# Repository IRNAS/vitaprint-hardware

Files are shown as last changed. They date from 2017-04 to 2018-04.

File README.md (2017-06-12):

# Vitaprint extruder

This repository containst files and descriptions for building a stepper-motor powered syringe extruder, which can be mounted on a general use CNC system. Feel free to fork and comment and if you have any questions, you [contact us](mailto:banovic@irnas.eu) directly. Contained in the repository you will find design files, a bill of materials, assembly instructions and extrusion calibration. To use the extruder within a CNC system, you will require CNC control electronics and software, which we do not provide. At Symbiolab the extruder was tested with [PlanetCNC](https://planet-cnc.com/).

## License 

All our projects are as usefully open-source as possible.

Hardware including documentation is licensed under [CERN OHL v.1.2. license](http://www.ohwr.org/licenses/cern-ohl/v1.2)

Firmware and software originating from the project is licensed under [GNU GENERAL PUBLIC LICENSE v3](http://www.gnu.org/licenses/gpl-3.0.en.html).

Open data generated by our projects is licensed under [CC0](https://creativecommons.org/publicdomain/zero/1.0/legalcode).

All our websites and additional documentation are licensed under [Creative Commons Attribution-ShareAlike 4 .0 Unported License] (https://creativecommons.org/licenses/by-sa/4.0/legalcode).

What this means is that you can use hardware, firmware, software and documentation without paying a royalty and knowing that you'll be able to use your version forever. You are also free to make changes but if you share these changes then you have to do so on the same conditions that you enjoy.

Symbiolab, Koruza, GoodEnoughCNC and IRNAS are all names and marks of Institut IRNAS Rače.
You may use these names and terms only to attribute the appropriate entity as required by the Open Licences referred to above. You may not use them in any other way and in particular you may not use them to imply endorsement or authorization of any hardware that you design, make or sell.



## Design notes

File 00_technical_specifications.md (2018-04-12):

# Vitaprint hardware technical specifications

## CNC XYZ mechanics: 3020T
- Machine size:
  -- Width: 410mm (X)
  -- Depth: 540mm (Y)
  -- Height: 400mm (Z)
- Motors (x, y, z):  NEMA23
- Movement resolution: 0.01mm (theoretically achievable 0.001mm)
- Motion drive: trapeziodal lead screw, linear rods with ball bearings
- Maximal number of extruders: 3

NOTE: The values above are for a default setup. Extrudes can be mounted on any 3-axis CNC platform, therefore the working area and maximal number of extruders can be changed if needed.

## Vitaprint extruder:
- Axis: 2
- Motion: Extruder Z movement and E extrusion
- Z motor: NEMA 11
- E motor: NEMA 11 with planetary gearbox
- Z movement resolution: 0.01mm (theoretically achievable 0.001mm)
- Cartridge: 5ml luer-lock syringes (polypropylene)
- Nozzle: Gauge needle
- Heating: room temperature - 250°C
- Extrusion resolution: 0.01mm piston movement (1.2uL for 5ml syringe)

## Control electronics:
- Controller: PlanetCNC MK3 9 axis
- Control software: PlanetCNC CNC USB controller
- Power Requirements: 230/110V AC
- Software: PlanetCNC CNC USB controller
- Operating Systems: Windows / Linux
- Print File Type: G-code

## Printing:
- Printing volume (x,y,z): 200 x 300 x 45mm
- Printing speed: max 2600mm/min, typical 500mm/min
- Print File Type: G-code (generate externally via Slic3r software)

NOTE: printing volume will depend on the amount of extruders used.

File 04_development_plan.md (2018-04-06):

# Vitaprint development plan:

## Biofabrication tools
- Microextrusion:
  * Piston driven syringe extrusion - standard syringes of various sizes (5 - 20ml)
  * Hydraulic syringe extrusion
  * Screw valve extrusion
- Core-shell printing
  * Needle in needle
- Multi-component printing
- Laser techniques
- Electrospinning
- Multiphoton polymerization
  
## Printer upgrades
- Thermoregulation: 
  * bed
  * nozzle
  * atmospheric chamber
- Bed: 
 * vacuum adhesion
 * dish positioning and adhesion
 * Autoleveling
- Monitoring:
  * Video microscope
  * Flow rate
  * Cartridge pressure

## Software add-ons and upgrades 
- g-code post-processing development for slicing software (eg. Slic3r, Cura,...)
- manual flow regulation of g-code embedded extrusion
- algorithmic extrusion linearization
- calibration protocols
- material optimization algortihms and methods
- Adaptive printing

## Fabrication protocol database
- Hydrogels
  * Gelatin
  * Collagen
  * Alginate
  * Chitosan
  * Gluten
  * Gellan gum  
  * Xanthan gum
  * Silk fibroin
  
- Pastes
  * Hydroxiapatite
  
- Polymers
  * Polycaprolactone
  * Polylactic acid

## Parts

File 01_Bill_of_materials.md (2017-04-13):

# Bill of materials

## Housing:
 - Aluminium plates (300mm x 400mm x 5mm)
 - Aluminium blocks:
   - SYRINGE MOUNT: block 35mm x 45mm x 70mm (minimum)
   - FRONT CAP: block 40mm x 12mm x 60mm (minimum)
   - 24BYJ48 NUT: block 15mm x 25mm x 30mm (minimum)
 - M3x12 DIN965 philips screw 10 pcs
 - M3x12 BN6404 torx sxrew 20pcs
 - 2 x fi3 stainless steel rod (L = 110mm)
 - 40mm x 8mm x 2mm rubber sheet

## Movement
 - Stepper motor Nema11 planetary (1:5 gear ratio)
 - 28BYJ48 unipolar motor ([modified into a bipolar motor] http://www.jangeox.be/2013/10/change-unipolar-28byj-48-to-bipolar.html )
 - Linear rail with carrige (L = 100mm)
 - Sliding rods (stainles steel, fi 3mm)
 - Brass spindle (M5x0.5mm, L = 90mm)
 - NUT: 3D printed 100% infill ABS block (28x28x55mm)

## Thermoregulation
 - Thermistor (read how to calibrate your own thermistor in the Calibration section)
 - 40W ceramic heater for 3D printers
 - 24V DC power supply
 - In our iteration we used PID thermoregulation algorithm (parameters need to be tuned by the user, depending on the control setup). Other temperature control systems can also be applied with this given hardware (relay switchin etc.).

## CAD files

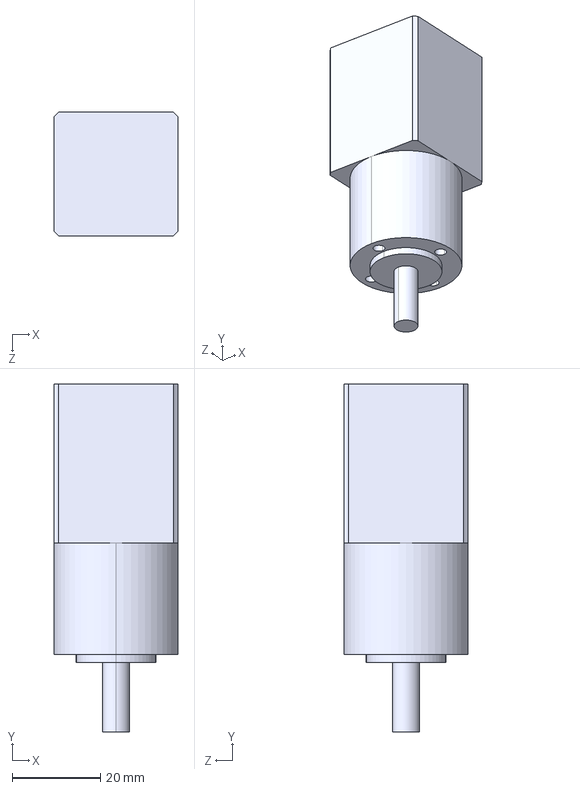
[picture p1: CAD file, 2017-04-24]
Build_files/Nema11_planetary.STEP
28.0 x 78.7 x 28.0 mm

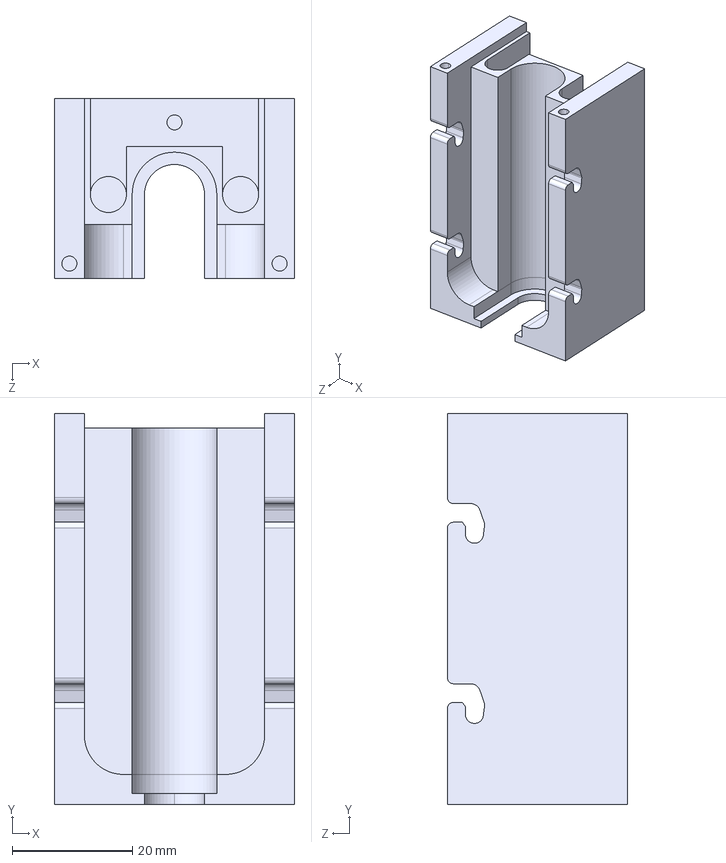
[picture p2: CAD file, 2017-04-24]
Build_files/syringe_mount.STEP
40.0 x 65.1 x 30.0 mm

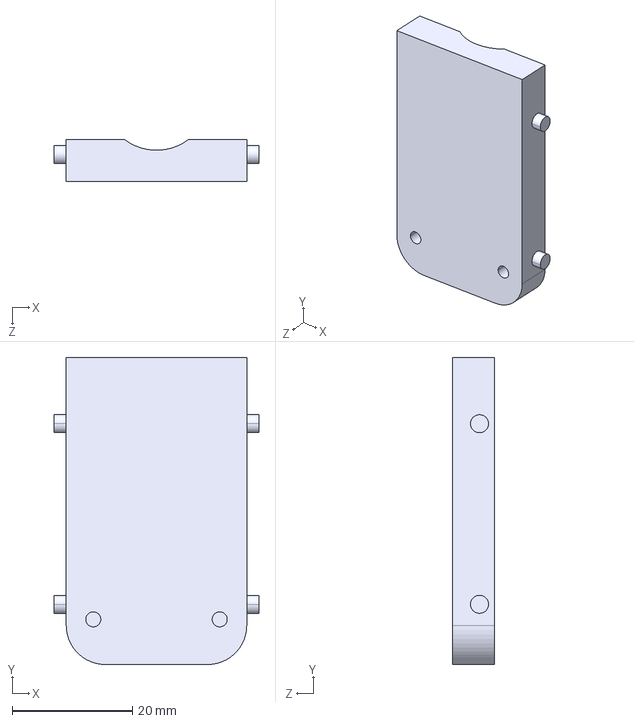
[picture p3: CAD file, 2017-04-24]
Build_files/front_cap.STEP
34.0 x 51.0 x 7.00 mm

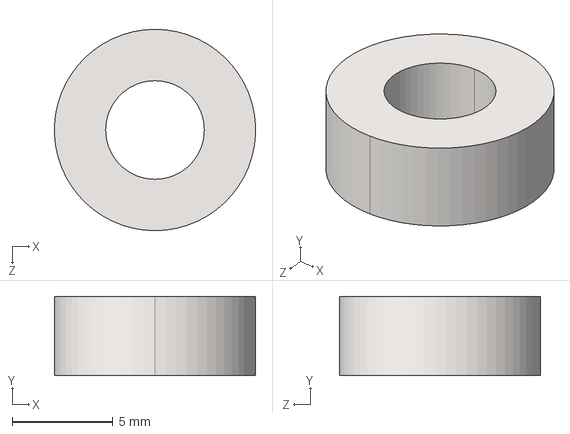
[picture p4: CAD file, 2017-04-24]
Build_files/rod_bearing.STEP
9.99 x 3.94 x 10.0 mm

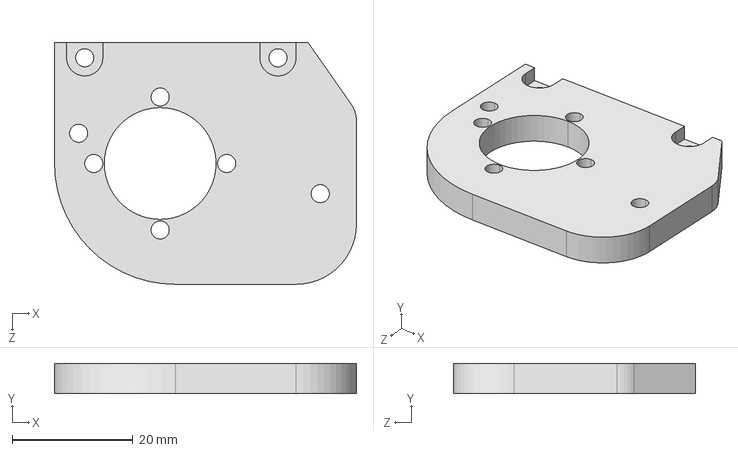
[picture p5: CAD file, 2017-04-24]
Build_files/N11-motor_plate_right.STEP
50.0 x 5.00 x 40.0 mm

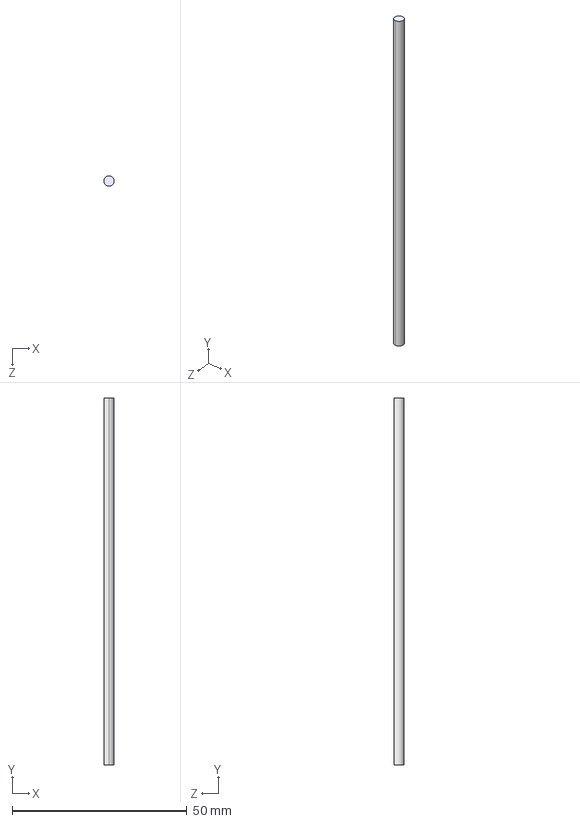
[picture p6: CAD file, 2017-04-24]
Build_files/rod fi3.STEP
3.00 x 105.0 x 3.00 mm

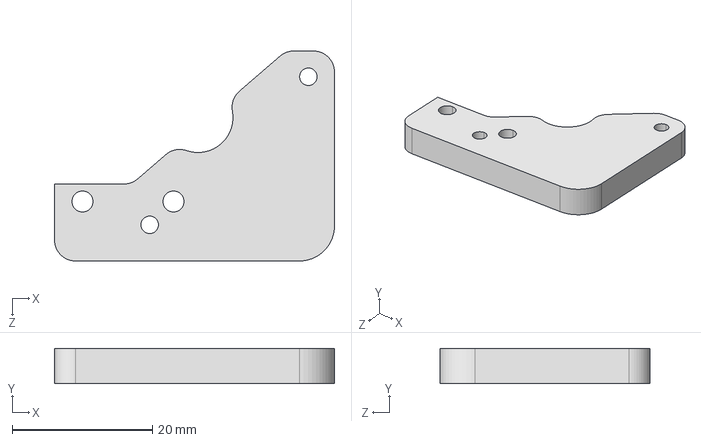
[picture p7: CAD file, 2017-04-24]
Build_files/24BYJ48-motor_plate_right.STEP
40.0 x 5.00 x 30.0 mm

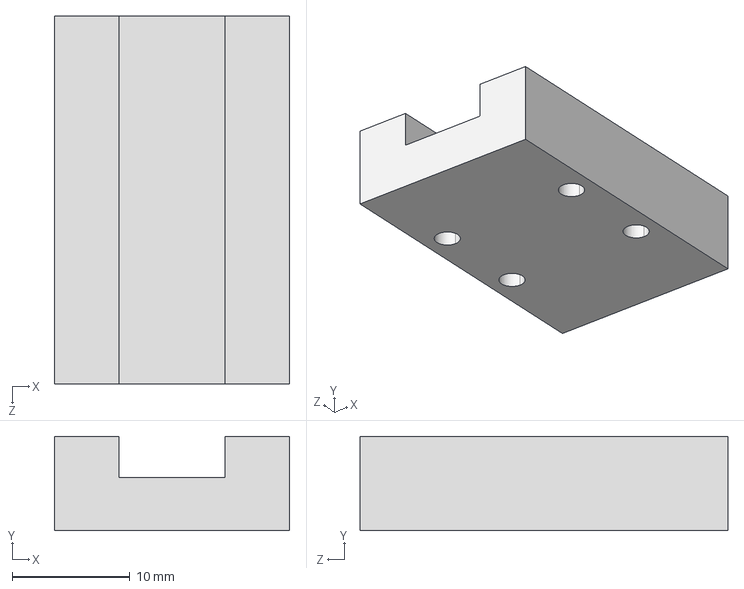
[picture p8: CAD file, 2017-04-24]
Build_files/trolley.STEP
20.0 x 8.00 x 31.3 mm

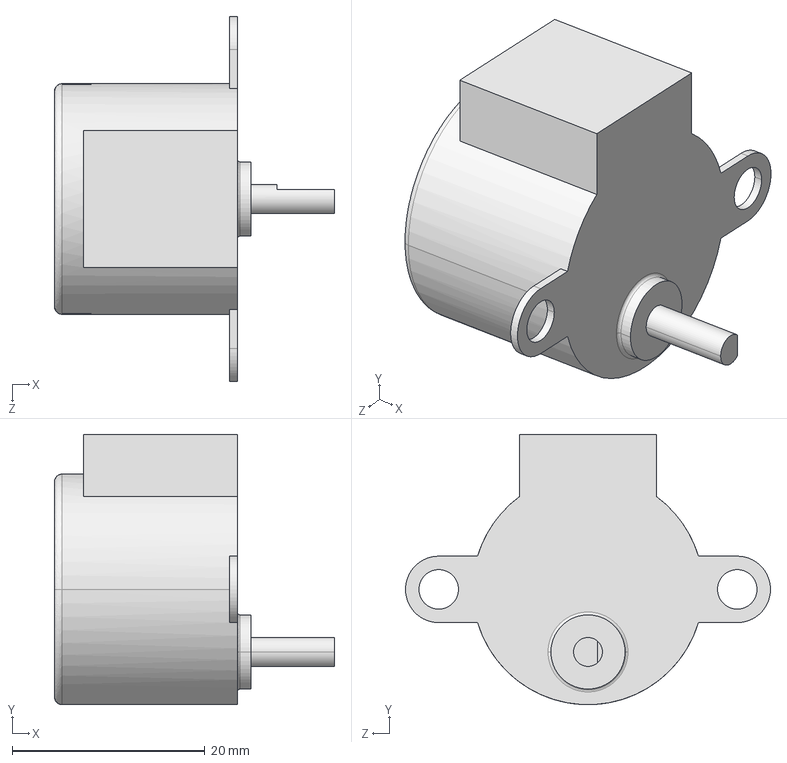
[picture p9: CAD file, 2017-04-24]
Build_files/24BYJ48-stepper.STEP
29.1 x 28.1 x 37.9 mm

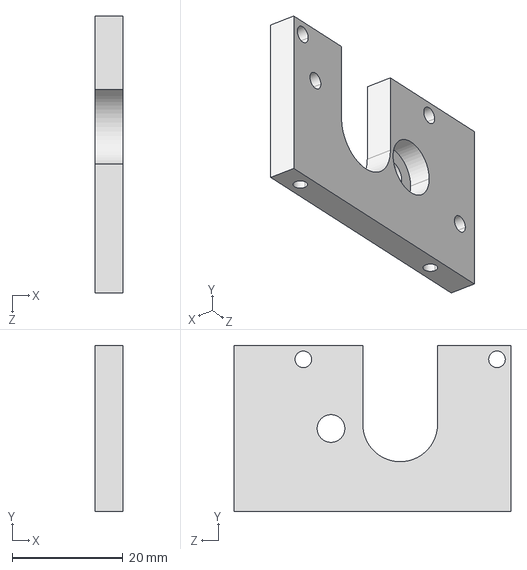
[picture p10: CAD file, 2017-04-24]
Build_files/rod_holder_right.STEP
5.00 x 30.0 x 50.0 mm

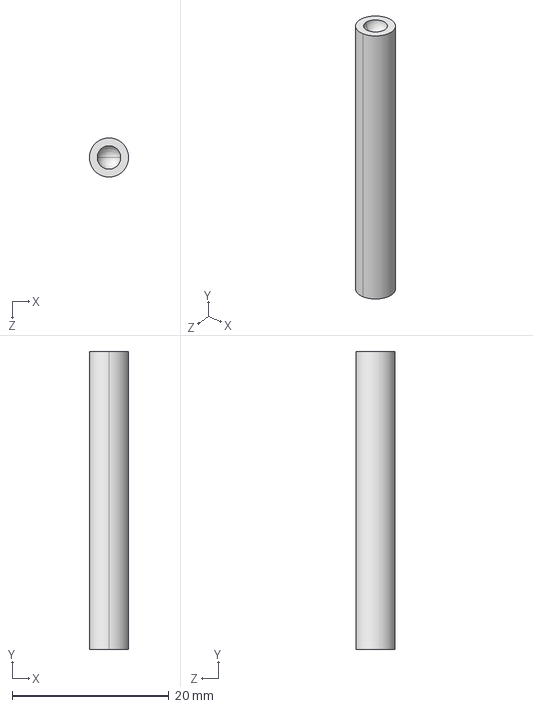
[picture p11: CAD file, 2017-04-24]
Build_files/24BYJ48_threaded_rod.STEP
5.00 x 38.0 x 5.00 mm

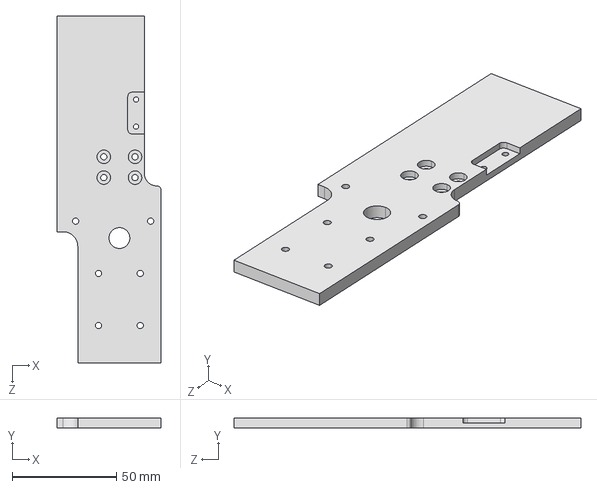
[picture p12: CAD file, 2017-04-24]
Build_files/backplate_right.STEP
50.0 x 5.00 x 166.6 mm

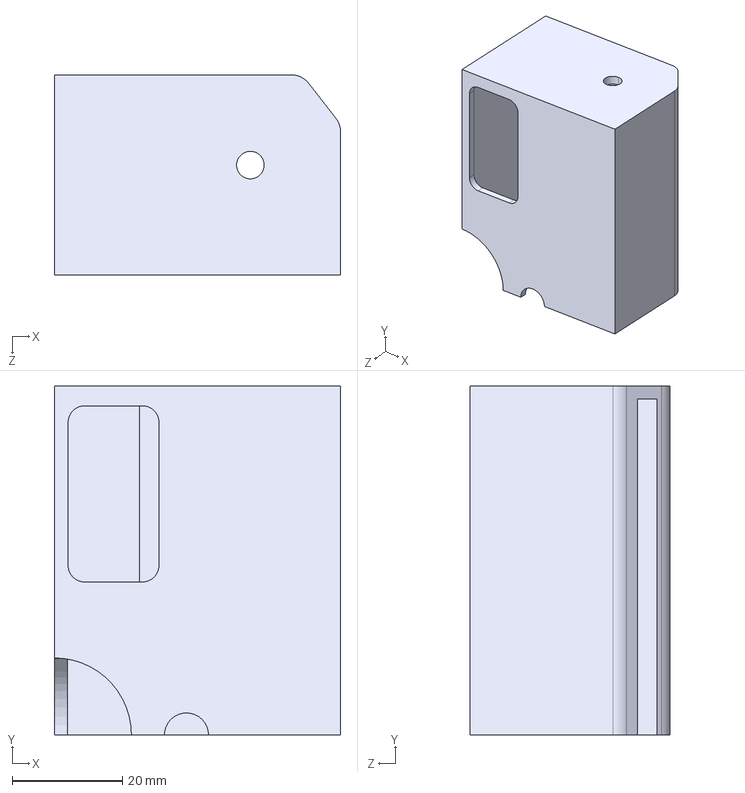
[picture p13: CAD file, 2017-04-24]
Build_files/cable_box-Mirror11.STEP
52.0 x 63.4 x 36.4 mm

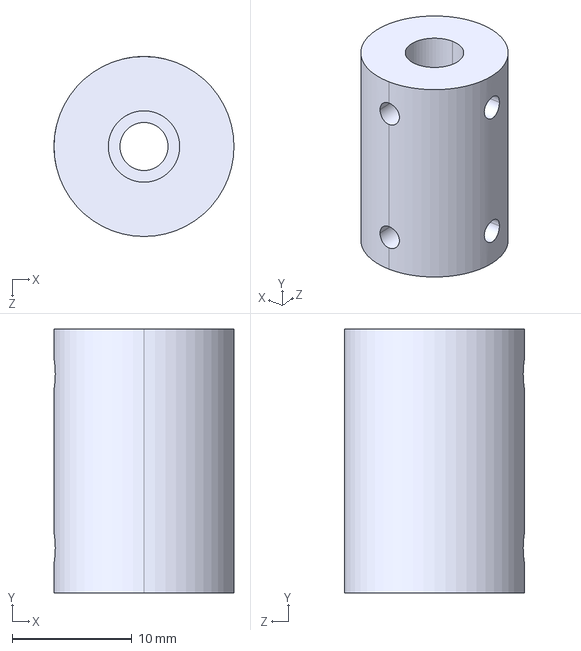
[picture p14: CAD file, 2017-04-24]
Build_files/coupler_extruder.STEP
15.0 x 22.0 x 15.0 mm

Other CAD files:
Build_files/N11-motor-plate_left.STEP
Build_files/24BYJ48-motor_plate_left.STEP
Build_files/backplate_left.STEP
Build_files/24BYJ48_nut.STEP
Build_files/Nut-block.STL
Build_files/cable_box-Boss-Extrude1.STEP
Build_files/nut - left.STEP
Build_files/nut - right.STEP
Build_files/nut_cover_plate_left.STEP
Build_files/nut_cover_plate_right.STEP
Build_files/rail.STEP
Build_files/rod_holder_left.STEP

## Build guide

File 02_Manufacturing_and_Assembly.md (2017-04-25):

# Manufacturing and Assembly

## Table of contents
 - [Overview](#OVER)
 - [Part Manufacturing](#MANUFACTURING)
 - [Assembly Brief](#ASSEMBLY)
 - [Arduino Temperature Regulation](#CODE)

## 1 Overview and Toolset 
Here you can find manufacturing and assembly details for one Vitaprint unit. In this repository you can find STEP files for the Vitaprint unit in both orientations - Left and Right. The procedure is the same for both orientations (the final product is only mirrored) therefore you will find details for assembly for one unit in this repository. 

### 1.1 General
- Manufacturing time: 7h
- Assembly time: 30 min
- Manufacturing skills: high

### 1.2 Tool List and Skills Required
 - 3D printer (ABS)
 - CNC mill
 - CNC router
 - band saw
 - lathe
 - HAND TOOLS:
   - torx srewdriver
   - phillips screwdriver
   - super glue
   - allan key
 
### 1.3 Necessary Steps
 - purchase of raw materials and components
 - manufacturing of parts
 - assembly
 - calibration
 
## 2 Part Manufacturing 
 - Manufacturing is impossible without advanced CNC milling and lathe skills.
 - The price of raw material depends on the quality/purity of material and contry of purchase. The kit price of manufactured parts would be approximately 250 USD.

 bubble

table

## 3 Assembly Details 

### 3.1 Assembly Overview
 - manufacture all parts
 - assembly details walk you through assembly of each section separately, then joining them together
 - Use philips DIN965 screws wherever you see the hole chamfers, use torx BN6404 screws elsewhere
 - for the following steps gently apply hammer:
   - sliding the M5 threaded rod into the coupler
   - sliding the fi3 stainless steel rod into rod holder at the bottom and N11 motor plate at the top

### 3.2 Assembly Details
 | DESCRIPTION | STEP 1 | STEP 2 | 
 |------|-------|-------|
 |Collect all parts and tools|tools_parts|
 |Take Nema11 motor plate and Nema11 stepper motor and fix them together with four torx screws|step1a|step1b|
 |Take the nut and nut plate and fix them together with two philips screws|step2a|step2b|
 |Take the threaded rod and join it with a coupler. The fit is designed to be tight.|step3a|step3b|
 |Screw the rod with a coupler through the nut M5 center thread. Slide the fi3 rods through the holes. |step4a|step4b|
  |Merge the N11 motor section and the nut-rod section.|step5a|step5b|
  |Take the syringe mount, syringe mount bottom and top plates.|step6||
  |Mount the bottom plate onto the syringe mount using two torx screws.|step7a|step7b|
  |Slide the ceramic heater in one of the bigger slots and place the thermistor in a smaller slot in the middle of syringe mount.|step8a|step8b|
  |Glue/weld the short M5 threaded rod onto the 24BYJ-48 shaft and place the 24BYJ-48 nut. Then fix the motor and nut to the backplate.|step9a|step9b|
  |Take the syringe mount and close it using torx screws and push the heater and thermistor wires through the wire slot in the backplate.|step10a|step10b|
  |Fix the syringe mount with hotend to the backplate.|step11a|step11b|
  |Mount the syringe mount - backplate assembly on to the CNC head. Begin with fixing the 24BYJ-48 to the respective motor plate.|step12a|step12b|
  |Continue with fixing the backplate to the rail of the linear bearing system.|step13a|step13b|
  |Mount the Nema11 assembly with extrusion mechanics (threaded rod, nut, linear sliding rods) to the top of the assembly. First slide the rods into the slods on the syringe mount top, then fix the Nema11 motor plate to the top of the backplacte using torx screws.|step14a|step14b|
  |This is the final appearance.|step15a|step15b|
  |Use superglue to stop rods sliding up and down when the nut is moved. Place the front cap into the slots to push the syringe towards the aluminium surroundings to prevent it from moving and to ensure good heat conduction.|step16|step16|

## 4 Arduino: Temperature Regulation 

To download Arduino firmware for temperature regulation please visit [vitaprint_heat_regulator](https://github.com/symbiolab/Vitaprint_heat_regulator). This is an external temperature control system and can be replaced by any system you may have available.

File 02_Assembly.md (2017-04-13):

# Assembly instructions

## Table of contents
 - [overview](#OvER)

 Tools, skills table, manufacturing time, assembly time
 
 - [Part list](#LIST)
 bubble photo
 
 - [Parts](#PARTS)
 manufacturing detail for each part
 
 - [arduino code](#CODE)
 Link to the vitaprint_heat_regulator

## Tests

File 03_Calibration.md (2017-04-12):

# Extruder calibration
To ensure the stepper movement translates into the piston movement accordingly to the g-code, it needs to be calibrated properly.

## Calibration set-up
In principle, the calibration set-up requires:
- CNC control of the piston powering motor (we use Nema 11 with a planetary reductor)
- the assembled extruder (at least the moving parts)
- a precise displacement measurement device (calipers, etc., high precision indicators are preferrable)

The calibration protocol requires a set-up, where the piston translation, can be precisely measured in the axis of extrusion. For this purpose, the measurement device is fixed on the extruder in a way, that the extruder movement is translated directly into the measurement.

## Calibration procedure
1. adjust the steps/unit value of the motor settings in the cnc control software (or use default values)
2. command piston movement for an exact distance
3. measure the real movement distance and compare
4. repeat steps 1-3, until the g-code value coincides with the measured value

For a Nema 11 motor (with a planetary reductor) + an M5 spindle (0.5mm pitch/rotation), the default STEPS/UNIT value is 37914.30.

# Thermistor calibration
Every thermistor analog output values have to be mapped to actual temperature values via an equation. Every thermistor needs to be calibrated as described in this section. 

EQUIPMENT: thermo block/plate (heat source), alcochol thermometer, thermistor, setup for reading analog signal from the thermistor, oil, glass.
1. pour a small glass of oil (50mL or so)
2. place the glass on the heat source
3. fit a thermistor to the alcochol thermometer
4. sink the thermistor - thermometer setup into the glass with oil
5. prepare the system to read analog values 
6. turn on the heat source and record sensor analog output at every 1°C increment
7. plot data (x - axis: analog output, y-axis: real temperature)
8. fit the best trendline to the data obtained (MATLAB or EXCEL are good tools for completing this task but there are also others)
9. software will yield a fit line equation which then has to be transcribed into microcontroller firmware (we used Arduino Mega)

Now your thermistor will give out the right temperature values.

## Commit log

2017-04-12 Create Assembly
2017-04-12 Create calibration
2017-04-12 Add files via upload
    This .zip file contains all STEP files for manufacturing and final assembly photos. NOTE: if you want to mount this double-extruder head on to your CNC system you will have to design and build a link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
2017-06-01 Add files via upload
    Vitaprint_generator.py generates the g-code for a simple scaffold and can be used as a testing tool for Vitaprint extruder. As a prerequisite you have to have Python 3 installed on your device in ord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
